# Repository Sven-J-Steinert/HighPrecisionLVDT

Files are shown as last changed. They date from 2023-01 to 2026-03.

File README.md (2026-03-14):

# HighPrecisionLVDT
This project is created during Praktikum Raumfahrtelektronik - Lehrstuhl für Raumfahrttechnik at the Technische Universität München (TUM).
This board carries out submicrometer measurement of an actuator displacement, which is part of a test-setup to transport Regolith via hoppers.
As a sensing unit an LVDT is used, that is driven by a Signal Conditioner which gets read by a 24-bit ADC to a MCU where the Experiment data is then delivered via USB.

Without any additional filtering a 3 sigma precision of `0.000161 mm` was achieved.

Contributors: [Beatriz Mas Sanz](https://github.com/beatrizmassanz), [Thilo Witzel](https://github.com/TheWisator) and [Sven Julius Steinert](https://github.com/Sven-J-Steinert)

# Application

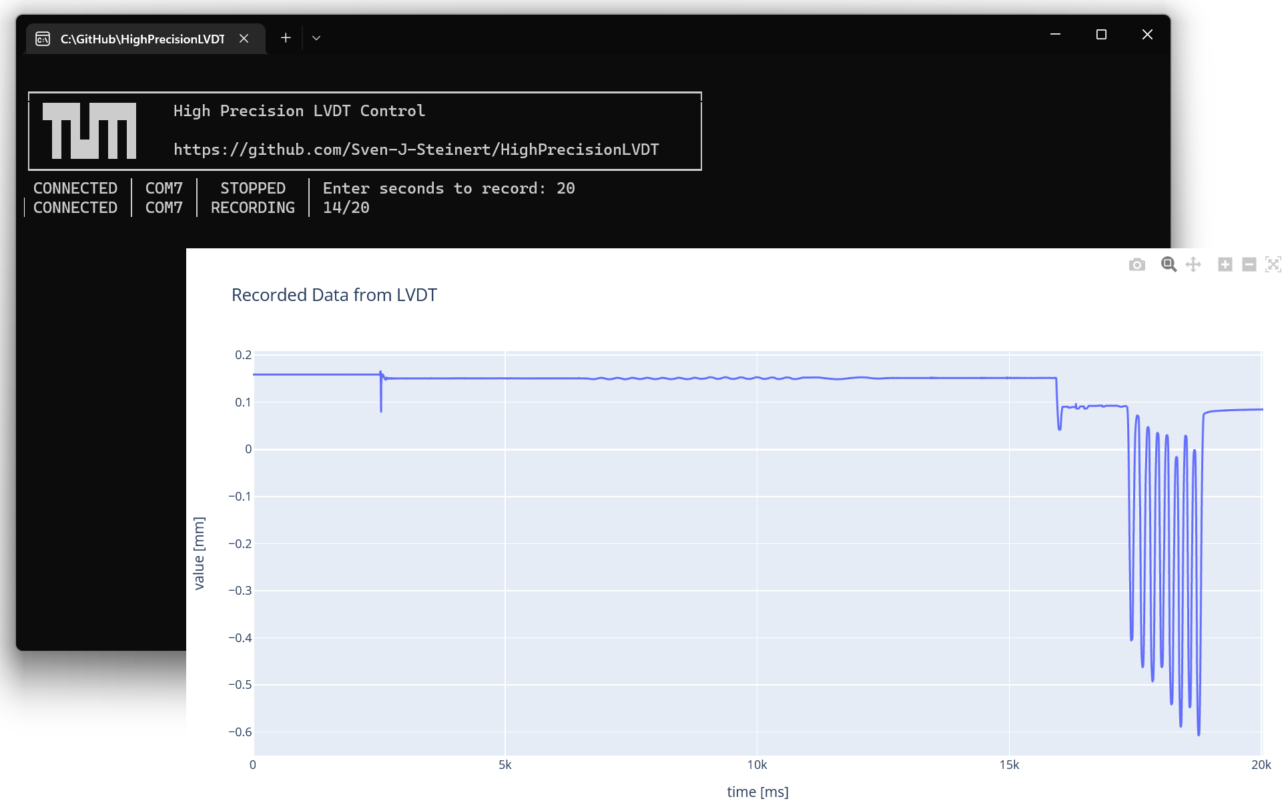
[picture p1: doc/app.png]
app




The Python app gives easy access to the recording functionality while autodetecting the device Port, saving the downloaded lines in data.csv and direct plotting via pyplot.

However, the MCU can also be controlled directly via COM Terminal at `baudrate = 921600` with the following commands

| CMD |	HEX | FUNCTION | ANSWER | 
| :---:   | :---:   | :---   | :---   |
| '0' |	0x48 | start recording | `RECORDING\nEND` | 
| '1' |	0x49 | stop recording | `STOPPED\nEND` | 
| '2' |	0x50 | start download | <.csv file> `END-OF-FILE-SEQUENCE\n` | 
| '3' |	0x51 | enable stream | `Stream Data Enabled` < values > | 
| '4' |	0x52 | disable stream | `Stream Data Disabled`  | 

The stream mode is supporting a higher sample rate at 500 sps (instead 200 sps in recording).
We recommend to use the streaming mode via [SerialPlot v0.12](https://hackaday.io/project/5334-serialplot-realtime-plotting-software/log/192838-serialplot-v012-release) where baudrate = 921600, and Data Format = ASCII have to be set before sending a '3' as starting Command.

# LVDT Hardware Connection

The PCB has to be connected to the LVDT sensor and a computer to operate. The power and data transmission for the LVDT are provided by a micro-USB connection.

| PCB Label | LVDT Cable | FUNCTION | 
| :---: | :---: | :---: |
| PYRD | Yellow - Red | Primary Coil | 
| PYBK | Yellow - Black | Primary Coil | 
| SBK | Black | Secondary Coil | 
| SRD | Red | Secondary Coil | 
| SBL | Blue | Secondary Coil |
| SGN | Green | Secondary Coil |

# Schematic
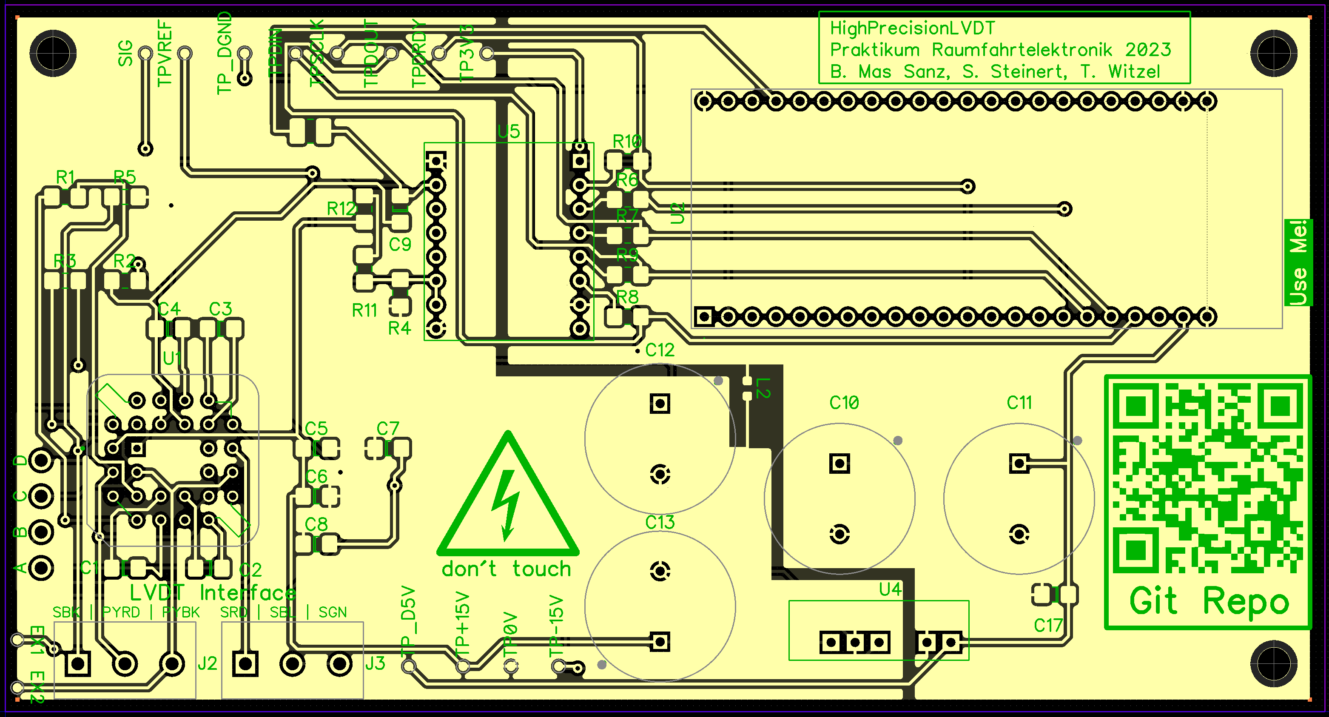
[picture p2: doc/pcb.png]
pcb

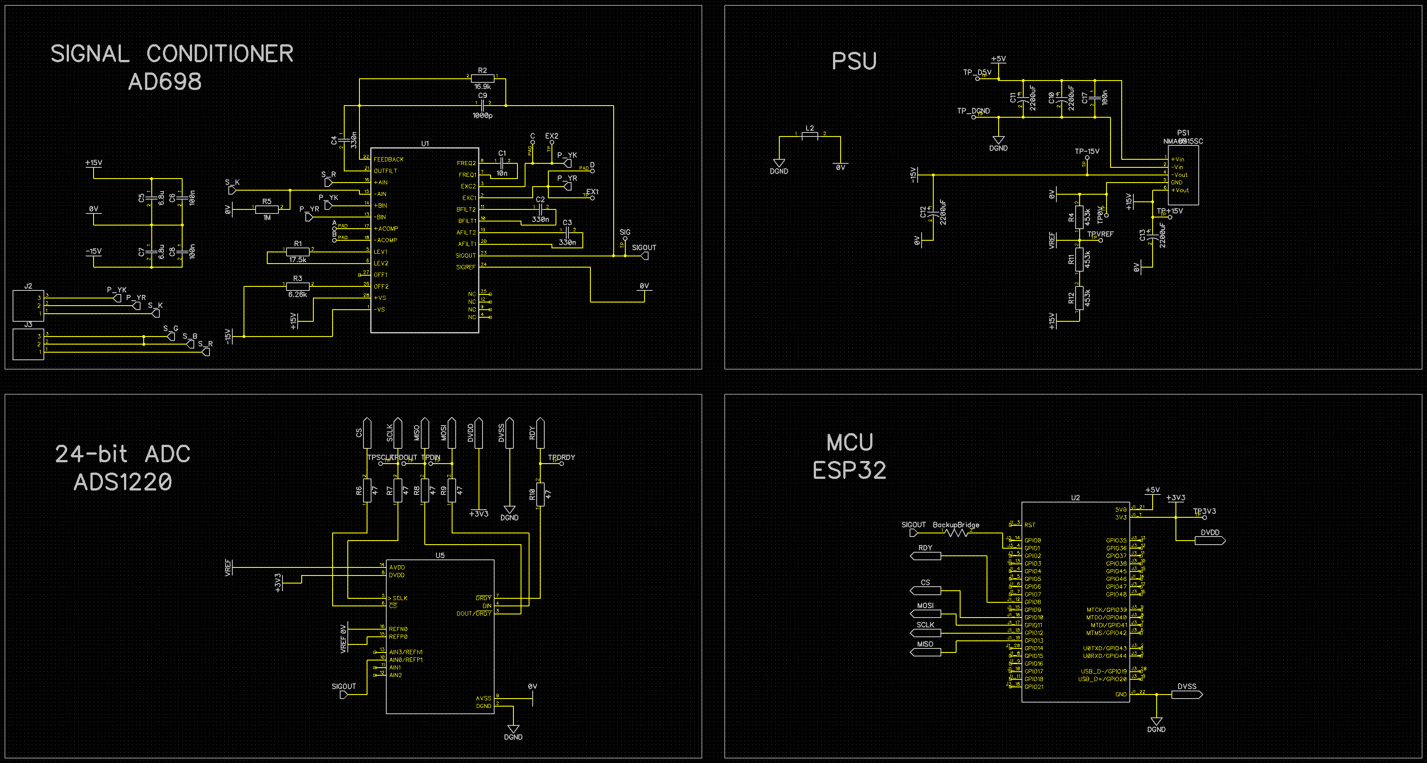
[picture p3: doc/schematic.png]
schematic


# Calibration

Since the linearity of the LVDT is proven in its factory test inspection and that linearity is conserved by the ADC a real calibration is not really meaningful.
Especially at this precision level, different kind of hardware than a digital Caliper is needed.

However, maximum positive and negative displacement of `± 1.27 mm` can be verified by its Voltage of `12.785418 mV` and `4362.785418 mV`.
If observed differently these mV values can be set in the MCU code.
The zero position of the sensor can be set through spinning the LVDT core on its positioning threaded screw.

# Partlist

|Mfr. No|Manufacturer|Description|Qty.|Price [EUR]|
|:----|:----|:----|----:|----:|
|02560389-000|TE Connectivity|Linear Displacement Sensors HR 050 LVDT .05in|1|166,31 |
|AD698APZ|Analog Devices Inc.|Sensor Interface LVDT SIGNAL CONDITIONER|1|54,27 |
|ADS1220IPWR|Olimex| BB-ADS1220 4 Channel Sigma Delta Precise 24-Bit ADC Breakboard | 1 | 13,00 |
|ESP32-S3-DevKitC-1-N8|Espressif|WiFi Development Tools - 802.11 ESP32-S3 General-Purpose Development Board, ESP32-S3-WROOM-1-N8, with Pin Header|1|15,00 |
|ERJ-8ENF1742V|Panasonic|Thick Film Resistors - SMD 1206 17.4Kohms 1% AEC-Q200|3|0,18 |
|ERA-8AEB1692V|Panasonic|Thin Film Resistors - SMD 1206 16.9Kohm 25ppm 0.1% AEC-Q200|3|0,66 |
|TNPW12066K26BEEN|Vishay|Thin Film Resistors - SMD 6.26Kohms .1% 25ppm|3|0,92 |
|HV732BTTD1004D|KOA Speer|Thick Film Resistors - SMD 0.25W 1M 0.5% 500 VOLTS|3|0,563 |
|C1206C104J1RACAUTO|KEMET|Multilayer Ceramic Capacitors MLCC - SMD/SMT 100V 0.1uF X7R 1206  5% AEC-Q200|13|0,199 |
|12065A102GAT4A|KYOCERA AVX|Multilayer Ceramic Capacitors MLCC - SMD/SMT 50V 1000pF C0G 1206 2% Tol|3|0,65 |
|12065C334JAT2A|KYOCERA AVX|Multilayer Ceramic Capacitors MLCC - SMD/SMT 50V 0.33uF X7R 1206 5%|7|0,491 |
|12062A102GAT2A|KYOCERA AVX|Multilayer Ceramic Capacitors MLCC - SMD/SMT 200V 1000pF C0G 1206 2% Tol|3|0,87 |
|PX-28LCC|Kycon|IC & Component Sockets LCC 28P PBT|2|1,75 |
|CR1206-FX-47R0ELF|Bourns|Thick Film Resistors - SMD 47ohm 1%|11|0,045 |
|CR0402-FX-4533GLF|Bourns|Thick Film Resistors - SMD CHIP RESISTOR|10|0,058 |
|B41888C4228M000|EPCOS / TDK|Aluminium Electrolytic Capacitors - Radial Leaded 16VDC 2200uF 20% STD Leads|4|1,89 |
|C1206C685K4PACTU|KEMET|Multilayer Ceramic Capacitors MLCC - SMD/SMT 16V 6.8uF X5R 1206 10%|5|0,87 |
|NMA0515SC|Murata|Isolated DC/DC Converters - Through Hole 1W  5-15V SIP DUAL DC/DC|2|5,08 |
|12063A103FAT2A|KYOCERA AVX|Multilayer Ceramic Capacitors MLCC - SMD/SMT 25V 0.01uF C0G 1206 1%|3|0,96 |

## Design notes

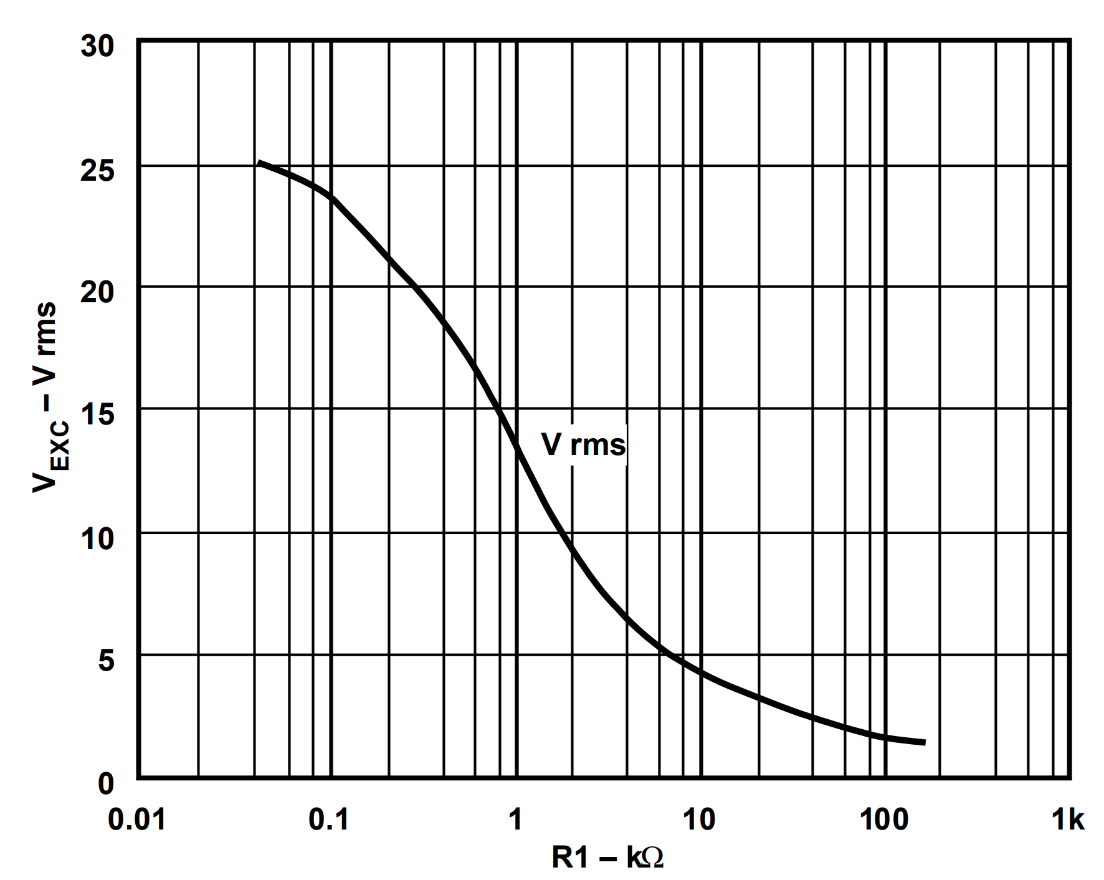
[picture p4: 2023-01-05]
doc/Signal-Conditioning/Vrms-R1.png

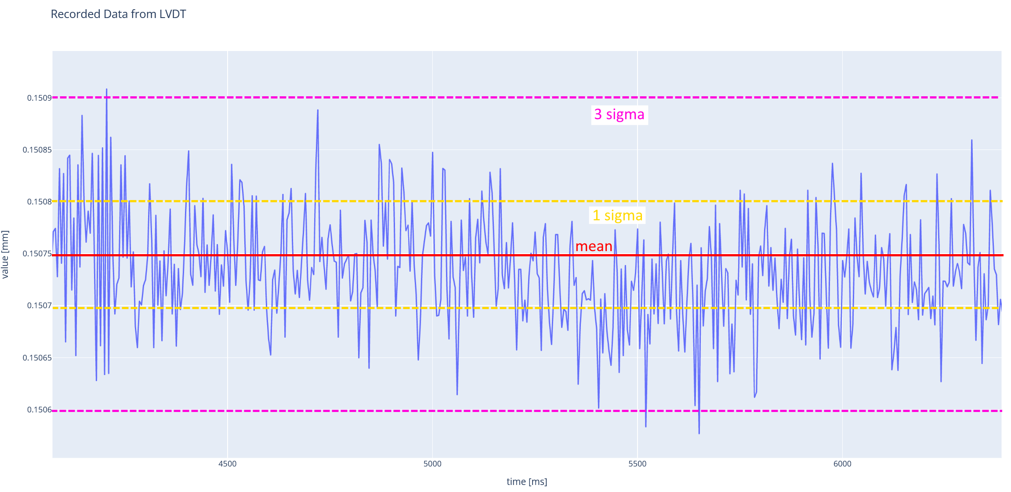
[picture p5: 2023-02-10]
doc/precision.png

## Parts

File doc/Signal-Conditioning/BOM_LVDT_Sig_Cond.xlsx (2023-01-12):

ID | DES | QTY | Value | Unit | Comment | Supplier | URL
1 | R1 | 1 | 17.4 | kΩ | SMD Resistor | Mouser | https://www.mouser.de/ProductDetail/Panasonic/ERJ-8ENF1742V?qs=s5eFII9cgBeXPstF9ITp4g%3D%3D
2 | R2 | 1 | 16.9 | kΩ | SMD Resistor | Mouser | https://www.mouser.de/ProductDetail/Panasonic/ERA-8AEB1692V?qs=sGAE
3 | R3 | 1 | 6.26 | kΩ | SMD Resistor | Mouser | https://www.mouser.de/ProductDetail/Vishay-Dale/TNPW12066K26BEEN
4 | R5 | 2 | 1 | MΩ | SMD Resistor | Mouser | https://www.mouser.de/ProductDetail/KOA-Speer/HV732BTTD1004D?qs=wRBQ8ZgBZ98lbzsHagWpKA%3D%3D
5 | C5/C7 | 2 | 6.8 | µF | Capacitor | Mouser | https://www.mouser.de/ProductDetail/KYOCERA-AVX/TAP685K035CRS
6 | C6/C8 | 2 | 100 | nF | SMD Capacitor | Mouser | https://www.mouser.de/ProductDetail/KEMET/C1206C104J1RACAUTO
7 | C1 | 1 | 10 | nF | SMD Capacitor | Mouser | https://www.mouser.de/ProductDetail/KYOCERA-AVX/12065A102GAT4A?qs=KpoduxKdAk3HwnytVN7DLg%3D%3D
8 | C2/C3/C4 | 3 | 330 | nF | SMD Capacitor | Mouser | https://www.mouser.de/ProductDetail/KYOCERA-AVX/12065C334JAT2A?qs=JsdQiTLDJHNcanErRX%252Br4Q%3D%3D
9 | C9 | 1 | 1 | nF | SMD Capacitor | Mouser | https://www.mouser.de/ProductDetail/KYOCERA-AVX/12062A102GAT2A?qs=mUWCwIpjqiwuO94FJZfzcQ%3D%3D
10 | U1 | 1 | - | - | AD698 | Mouser
11
12
13
14
15
16
17
18
19
20
21
22
23
24
25
26
27

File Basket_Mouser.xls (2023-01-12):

SHOPPING BASKET
This is not an invoice
12-Jan-23 13:46:31
 | Mouser No | Mfr. No | Manufacturer | Customer No | Description | RoHS | Lifecycle | Order Qty. | Price (EUR) | Ext.: (EUR)
1 | 667-ERJ-8ENF1742V | ERJ-8ENF1742V | Panasonic |  | Thick Film Resistors - SMD 1206 17.4Kohms 1% AEC-Q200 | RoHS Compliant By Exemption | NRND | 3 | 0,18 € | 0,54 €
2 | 667-ERA-8AEB1692V | ERA-8AEB1692V | Panasonic |  | Thin Film Resistors - SMD 1206 16.9Kohm 25ppm 0.1% AEC-Q200 | RoHS Compliant By Exemption |  | 3 | 0,66 € | 1,98 €
3 | 71-TNPW12066K26BEEN | TNPW12066K26BEEN | Vishay |  | Thin Film Resistors - SMD 6.26Kohms .1% 25ppm | RoHS Compliant |  | 3 | 0,92 € | 2,76 €
4 | 660-HV732BTTD1004D | HV732BTTD1004D | KOA Speer |  | Thick Film Resistors - SMD 0.25W 1M 0.5% 500 VOLTS | RoHS Compliant By Exemption |  | 3 | 0,563 € | 1,69 €
5 | 80-C1206C104J1RAUTO | C1206C104J1RACAUTO | KEMET |  | Multilayer Ceramic Capacitors MLCC - SMD/SMT 100V 0.1uF X7R 1206 5% AEC-Q200 | RoHS Compliant | New Product | 13 | 0,199 € | 2,59 €
6 | 581-12065A102GAT4A | 12065A102GAT4A | KYOCERA AVX |  | Multilayer Ceramic Capacitors MLCC - SMD/SMT 50V 1000pF C0G 1206 2% Tol | RoHS Compliant |  | 3 | 0,65 € | 1,95 €
7 | 581-12065C334JAT2A | 12065C334JAT2A | KYOCERA AVX |  | Multilayer Ceramic Capacitors MLCC - SMD/SMT 50V 0.33uF X7R 1206 5% | RoHS Compliant By Exemption |  | 7 | 0,491 € | 3,44 €
8 | 581-12062A102GAT2A | 12062A102GAT2A | KYOCERA AVX |  | Multilayer Ceramic Capacitors MLCC - SMD/SMT 200V 1000pF C0G 1206 2% Tol | RoHS Compliant |  | 3 | 0,87 € | 2,61 €
9 | 584-AD698APZ | AD698APZ | Analog Devices Inc. |  | Sensor Interface LVDT SIGNAL CONDITIONER | RoHS Compliant |  | 1 | 54,27 € | 54,27 €
10 | 806-PX-28LCC | PX-28LCC | Kycon |  | IC & Component Sockets LCC 28P PBT | RoHS Compliant |  | 2 | 1,75 € | 3,50 €
11 | 824-02560389-000 | 02560389-000 | TE Connectivity |  | Linear Displacement Sensors HR 050 LVDT .05in | RoHS Compliant |  | 1 | 166,31 € | 166,31 €
12 | 652-CR1206FX-47R0ELF | CR1206-FX-47R0ELF | Bourns |  | Thick Film Resistors - SMD 47ohm 1% | RoHS Compliant By Exemption |  | 11 | 0,045 € | 0,50 €
13 | 652-CR0402FX4533GLF | CR0402-FX-4533GLF | Bourns |  | Thick Film Resistors - SMD CHIP RESISTOR | RoHS Compliant By Exemption |  | 10 | 0,058 € | 0,58 €
14 | 871-B41888C4228M000 | B41888C4228M000 | EPCOS / TDK |  | Aluminium Electrolytic Capacitors - Radial Leaded 16VDC 2200uF 20% STD Leads | RoHS Compliant |  | 4 | 1,89 € | 7,56 €
15 | 356-ESP32-S3DVKTC1N8 | ESP32-S3-DevKitC-1-N8 | Espressif |  | WiFi Development Tools - 802.11 ESP32-S3 General-Purpose Development Board, ESP32-S3-WROOM-1-N8, with Pin Header |  | New Product | 1 | 15,00 € | 15,00 €
16 | 356-ESS3DVKTC1N32R8V | ESP32-S3-DevKitC-1-N32R8V | Espressif |  | WiFi Development Tools - 802.11 Gen-Purpose Dev Bd, embeds ESP32-S3-WROOM-2-N32R8V, 32 MB Octal flash & 8 MB Octal PSRAM, w/ Pin Header | RoHS Compliant | New Product | 1 | 18,00 € | 18,00 €
17 | 80-C1206C685K4P | C1206C685K4PACTU | KEMET |  | Multilayer Ceramic Capacitors MLCC - SMD/SMT 16V 6.8uF X5R 1206 10% | RoHS Compliant |  | 5 | 0,87 € | 4,35 €
18 | 580-NMA0515SC | NMA0515SC | Murata |  | Isolated DC/DC Converters - Through Hole 1W 5-15V SIP DUAL DC/DC | RoHS Compliant By Exemption |  | 2 | 5,08 € | 10,16 €
19 | 581-12063A103F | 12063A103FAT2A | KYOCERA AVX |  | Multilayer Ceramic Capacitors MLCC - SMD/SMT 25V 0.01uF C0G 1206 1% | RoHS Compliant |  | 3 | 0,96 € | 2,88 €
By submitting your order you agree to these terms and conditions. (https://www.mouser.de/saleterms) |  |  |  |  |  |  |  |  | Merchandise: | 300,67 €
Prices are reflected at the date and time shown. |  |  |  |  |  |  |  |  | Delivery Charge: | 0,00 €

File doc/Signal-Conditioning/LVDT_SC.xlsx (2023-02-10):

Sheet: Sheet1
A | Oscillator Frequency |  |  | Summary
f_sub | 344.8 | Hz | Desired measurement frequency | R1 | 17.50 | kΩ
f_exc | 3448 | Hz | Excitation Frequency | R2 | 15.02 | kΩ
C1 | 1.015081206e-08 | F | Capacitor C1 | R3 | 6.24 | kΩ
B | Oscillator Amplitude |  |  | R4 | 1e+99 | kΩ
S | 228 | mV/V/mm | LVDT Sensitivity | C1 | 10.15081206 | nF
d_max | 1.27 | mm | Max stroke length from null | C2 | 319.025522 | nF
VTR | 289.56 | mV/V | Voltage transformation Ratio | C3 | 319.025522 | nF
U_exc_max | 3 | Vrms | Max Excitation Voltage | C4 | 319.025522 | nF
U_sec_max | 0.86868 | Vrms | Mac Secondary Voltage
R1 | 17.5 | kΩ | R1 (see chart) | C1 | 1.015e-08 | F
C2 | 3.19025522e-07 | F | Capacitor for System Bandwidth | f_exc | 3448.275862 | Hz
C3 | 3.19025522e-07 | F | Capacitor for System Bandwidth
C4 | 3.19025522e-07 | F | Capacitor for System Bandwidth
D | Full-Scale Output Voltage
U_out ± | 2.175 | Vdc | Output Voltage | Umin | 0.01278541798 | V
R2 | 15.0227932 | kΩ | Resistor R2 | Umax | 4.362785418 | V
E.1 | Positive Output Voltage Offset
U_os | 2.175 | Vdc | Offset Voltage
R3 | 6.28843763 | kΩ
R4 | inf | kΩ
E.2 | Negative Output Voltage Offset
U_os | -2.175 | Vdc | Offset Voltage
R3 | inf | kΩ
R4 | 6.28843763 | kΩ
E.3 | Output Voltage Offset Both Resistors
U_os | 2.187785418 | Vdc | Offset Voltage
R3 | 6.24 | kΩ
R4 | 1e+99 | kΩ
F | Phase Shift Adjustment
φ | -1 | ° | LVDT Primary to Secondary Phase Shift
Rt | 10000 | Ω
Rs | 1e-07 | Ω
R | 10000000 | Ω
C | 1e-15 | F
Lag | 0.001975558477 | °
Lead | 89.99802444 | °

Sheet: Sheet2
R1 [kOhm] | U_exc [Vrms] |  | 3.5
7.362275922 | 4.912663755
8.631707567 | 4.585152838
10.53058515 | 4.257641921 | 17.31178975 | 3.537117904
12.84719423 | 3.930131004 | 20.29675445 | 3.27510917
14.76581219 | 3.733624454
17.31178975 | 3.537117904
20.29675445 | 3.27510917
24.27430502 | 3.07860262 | 24.27430502 | 3.07860262
28.45977311 | 2.88209607 | 28.45977311 | 2.88209607
32.70999544 | 2.68558952
39.12016617 | 2.489082969 | 24.27799539 | 3
46.78653667 | 2.292576419
55.95528413 | 2.096069869
66.92082905 | 1.965065502
81.64265106 | 1.768558952
112.224158 | 1.506550218

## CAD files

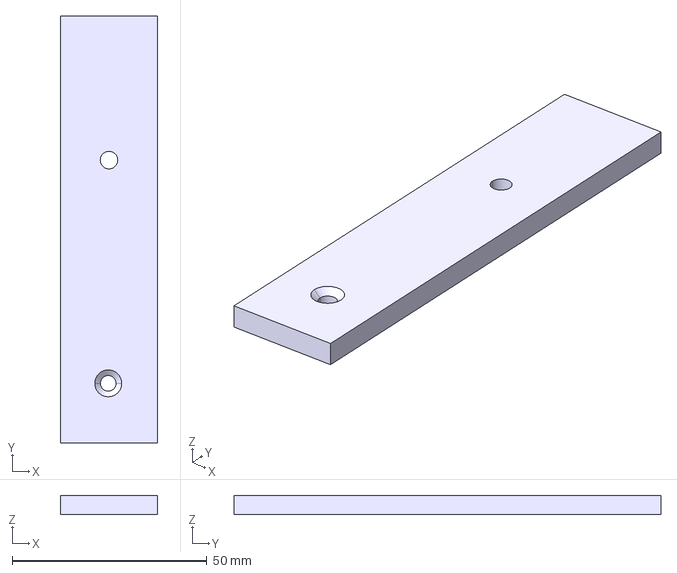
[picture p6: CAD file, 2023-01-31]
Mounting/Top.stp
25.0 x 109.6 x 5.00 mm

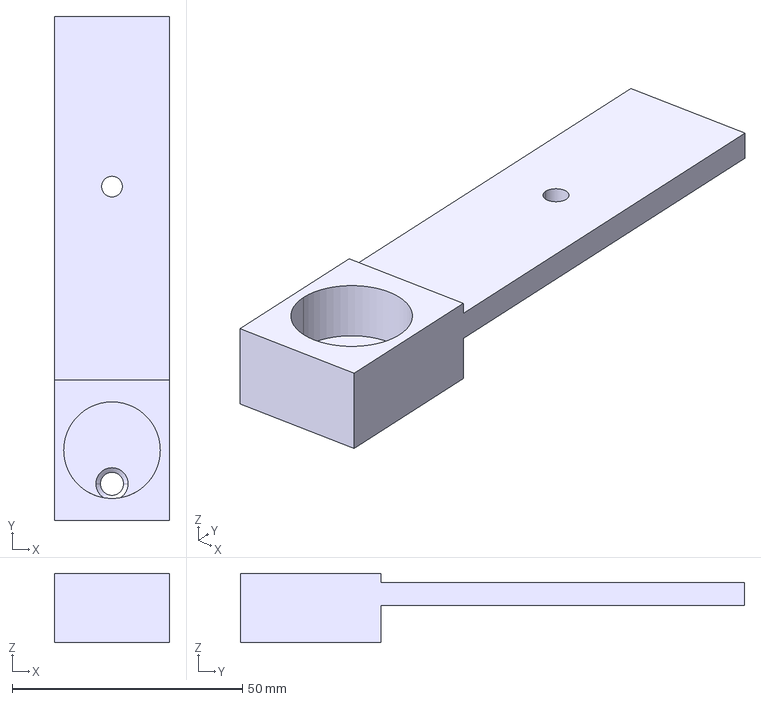
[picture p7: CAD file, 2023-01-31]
Mounting/Bottom.stp
25.0 x 109.6 x 15.0 mm

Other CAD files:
Mounting/Bottom.stl
Mounting/Top.stl

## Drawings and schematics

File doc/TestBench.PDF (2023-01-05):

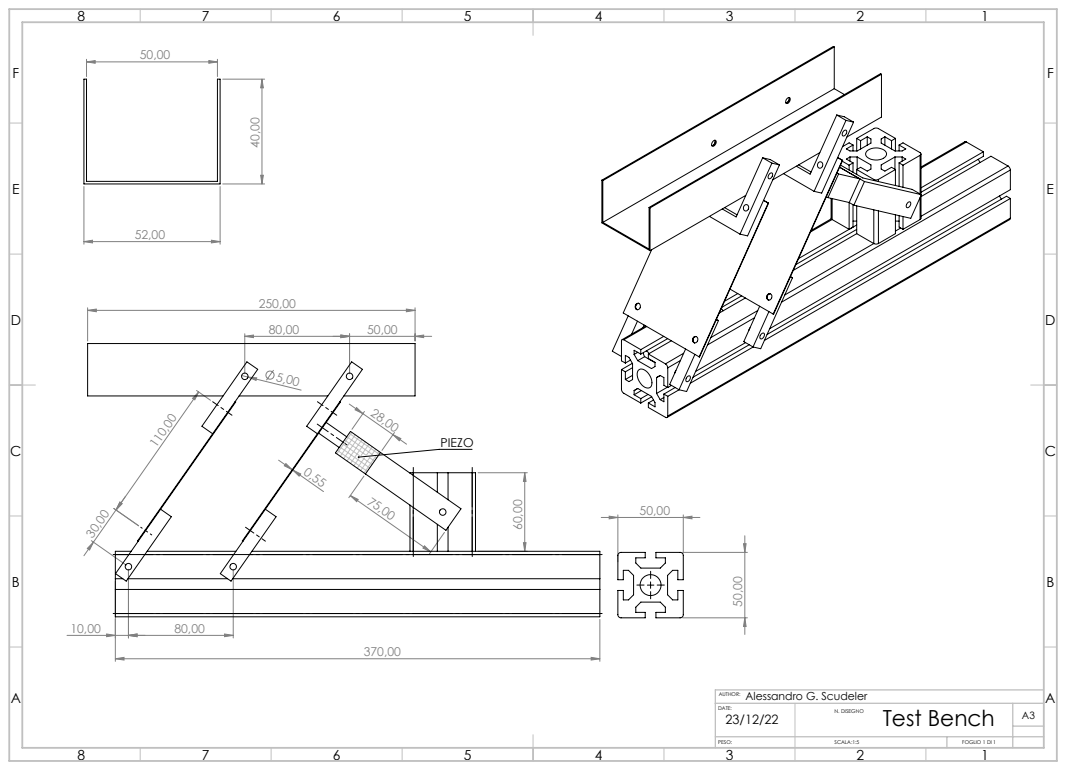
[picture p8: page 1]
N. DISEGNO; SCALA:1:5; FOGLIO 1 DI 1

AUTHOR: Alessandro G. Scudeler
Test Bench DATE:

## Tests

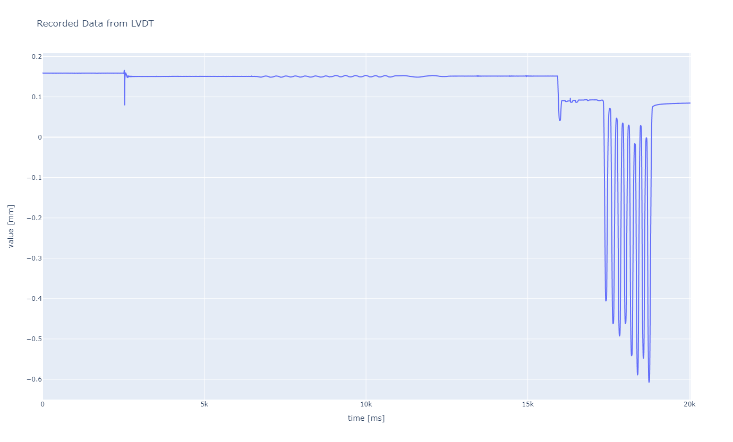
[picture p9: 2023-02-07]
doc/testplot.png

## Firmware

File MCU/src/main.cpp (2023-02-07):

#include <Arduino.h>
#include <ADS1220_WE.h>
#include <SPI.h>

// 24-bit ADC
#define ADS1220_CS_PIN    10 // chip select pin
#define ADS1220_DRDY_PIN  8 // data ready pin 

ADS1220_WE ads = ADS1220_WE(ADS1220_CS_PIN, ADS1220_DRDY_PIN); // using Default SPI Pins

// RAM Storage
#define RAM_STORAGE_SIZE 12000 // with 200 [Hz] results in 60 [s] max
long *time_RAM; // 4 Bytes per entry
double *value_RAM; // 4 Bytes per entry

int index_RAM = 0;
double val_buffer;
double time_buffer;
char val_buffer_str[50];

byte incomingByte = 0; // for incoming serial data
String header = "time [ms],value [mm]\n" ; // table head
String databuffer = "" ; // buffer for recording data

bool record = false;
bool stream = false;
unsigned long ref_time = 0;
double value = 0.0;
ulong last_measure = 0;

// define LVDT IC circuit properties
const double U_min = 12.785418;  // minimum DC voltage of LVDT IC in mV
const double U_max = 4362.785418;  // maximum DC voltage of LVDT IC in mV
const double disp_range = 1.27;    // displacement measurement range in mm (+- 1.27mm)
//const float dU_dd = (U_max - U_min) / (disp_range);   // gradient VDc over displacement in VDC / mm

// define LVDT properties
const double sensitivity = 5777.8 / 25.4;  // LVDT sensitivity in mV/Vrms/mm
const double U_0 = 0.004;                  // LVDT null voltage in Vrms
const double U_exc = 3.5;                  // LVDT excitation voltage in Vrms

void setup() {
  // MCU bootinfo during startup is passed in 115200 baudrate
  Serial.begin(921600); // very high speed, no bitloss observed however
  // dynamically Allocate 48kB of RAM for time_RAM
  time_RAM = new long[RAM_STORAGE_SIZE];
  // dynamically Allocate 48kB of RAM for value_RAM
  value_RAM = new double[RAM_STORAGE_SIZE];
  // initialize ADC
  if(!ads.init()){
    Serial.println("ERROR | ADS1220 not found!"); // should hopefully never occur
    while(1);
  }
  ads.bypassPGA(true);
  ads.setRefp0Refn0AsVefAndCalibrate();
  ads.setCompareChannels(ADS1220_MUX_0_AVSS); // measure IN0 to AVSS (AVDD as max value)
  ads.setDataRate(ADS1220_DR_LVL_6);
}

double mapfloat(double x, double in_min, double in_max, double out_min, double out_max){
  return (double)(x - in_min) * (out_max - out_min) / (double)(in_max - in_min) + out_min;
}

double measure_displacement(double ADC_voltage){
  // input: ADC voltage in mV
  // output: displacement in mm
  double displacement = mapfloat(ADC_voltage, U_min, U_max, -disp_range, disp_range);
  return displacement;
}

void loop() {

  if (record){
    if(index_RAM < RAM_STORAGE_SIZE && millis()>=last_measure+5){
      last_measure = millis();
      // read ADC
      value = measure_displacement(ads.getVoltage_mV());
      // prepare value and time to write
      time_buffer = (millis()-ref_time);
      val_buffer = value;

      time_RAM[index_RAM] = time_buffer;
      value_RAM[index_RAM] = val_buffer;
      ++index_RAM;

      // could've been also done via interrupts for more accurate timing performance
      // interrupts not implemented due to missing necessity
      }
    }
  else if (stream && millis()>=last_measure+2){
    last_measure = millis();
    // read ADC
    val_buffer = measure_displacement(ads.getVoltage_mV());
    dtostrf(val_buffer, 10, 8, val_buffer_str);
    Serial.println(val_buffer_str);
  }

  if (Serial.available() > 0) {
    // read the incoming byte:
    incomingByte = Serial.read();

    switch(incomingByte) {
      case 48:
        // Start Recording = '0' = 48 [ASCII]
        index_RAM = 0; // reset buffer
        Serial.print("RECORDING");
        Serial.print("\nEND");
        record = true;
        stream = false;
        ref_time = millis()+1;
        break;
      case 49:
        // Stop Recording = '1' = 49 [ASCII]
        Serial.print("STOPPED");
        Serial.print("\nEND");
        record = false;
        stream = false;
        break;
      case 50:
        // Start Download = '2' = 50 [ASCII]
        Serial.print("DOWNLOAD");
        Serial.print("\nEND");
        
        Serial.print(header);
        for (int i = 0; i < index_RAM; ++i)
          {
            Serial.print(time_RAM[i]);
            Serial.print(',');
            dtostrf(value_RAM[i], 10, 8, val_buffer_str);
            Serial.print(val_buffer_str);
            Serial.print('\n');
          }
        
        Serial.print("END-OF-FILE-SEQUENCE\n");
        break;
      case 51:
        // Enable Stream Data = '3' = 51 [ASCII]
        stream = true;
        Serial.println("Stream Data Enabled");
        break;
      case 52:
        // Disable Stream Data = '4' = 52 [ASCII]
        stream = false;
        Serial.println("Stream Data Disabled");
      default:
        break;
    }
  }
}

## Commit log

2023-01-05 Signal Conditioning Section
    -Circuit / Schematic
    -Calculations for Resistors and Capacitors
    -BOM
    [BOM_LVDT_Sig_Cond.xlsx, LVDT_SC.xlsx]
2023-01-06 Capacitor Mouser
2023-01-06 Inserted PCU into Main Schematic
2023-01-12 Update BOM
    [BOM_LVDT_Sig_Cond.xlsx, LVDT_SC.xlsx]
2023-01-12 Mouser Order
    [Basket_Mouser.xls]
2023-01-14 prototype app + mcu
2023-01-19 ESP32S3 MCU
2023-01-24 PCB print
2023-02-07 MCU add voltage-displacement conversion
2023-02-07 Meeting 2023-02-07
    [LVDT_SC.xlsx, data.csv]
